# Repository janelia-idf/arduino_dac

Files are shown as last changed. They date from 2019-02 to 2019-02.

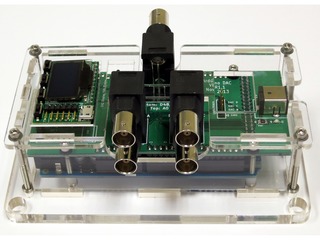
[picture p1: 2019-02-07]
images/arduino_dac_04_s.jpg

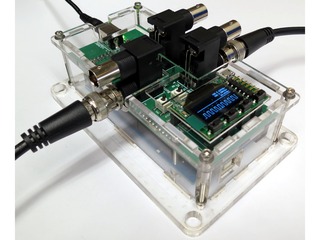
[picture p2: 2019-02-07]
images/arduino_dac_08_s.jpg

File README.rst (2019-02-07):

===========
Arduino DAC
===========

Arduino-based digital to analog converter.

firmware
========

Contains the Arduino firmware files. See firmware/README.rst

host
====

Contains the code for controlling with a host computer.

python
------

See host/python/README.rst

pcb
===

Contains the arduino_dac pcb Kicad and gerber files.

Author: Peter Polidoro

This program is free software: you can redistribute it and/or modify
it under the terms of the GNU Lesser General Public License as published by
the Free Software Foundation, either version 3 of the License, or
(at your option) any later version.

This program is distributed in the hope that it will be useful,
but WITHOUT ANY WARRANTY; without even the implied warranty of
MERCHANTABILITY or FITNESS FOR A PARTICULAR PURPOSE.  See the
GNU Lesser General Public License for more details.

You should have received a copy of the GNU Lesser General Public License
along with this program.  If not, see <http://www.gnu.org/licenses/>.

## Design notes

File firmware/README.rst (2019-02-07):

Arduino DAC Device Firmware
---------------------------

Arduino firmware for the arduino_dac device.

For see the INSTALL.rst for installation instructions.

arduino_relay_controller device firmware may be freely distributed and
modified in accordance with the License.

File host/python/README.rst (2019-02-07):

===========
arduino_dac
===========

arduino_dac is a python package to control the Arduino DAC over USB,
using the python module, the command line, or a webpage using a
webserver.

Install
-------

See INSTALL.rst

Running
=======

* If installed into a virtual environment, activate the virtual
  environment before running::

    source ~/virtualenvs/arduino_dac/bin/activate

Python Module
-------------

Typical usage often looks like this::

    from arduino_dac import ArduinoDac

Web Page Controls
-----------------

Open a terminal and run::

    arduino_dac_webserver.py

Open a browser and navigate to::

    http://localhost:5000

Author: Peter Polidoro

This program is free software: you can redistribute it and/or modify
it under the terms of the GNU Lesser General Public License as published by
the Free Software Foundation, either version 3 of the License, or
(at your option) any later version.

This program is distributed in the hope that it will be useful,
but WITHOUT ANY WARRANTY; without even the implied warranty of
MERCHANTABILITY or FITNESS FOR A PARTICULAR PURPOSE.  See the
GNU Lesser General Public License for more details.

You should have received a copy of the GNU Lesser General Public License
along with this program.  If not, see <http://www.gnu.org/licenses/>.

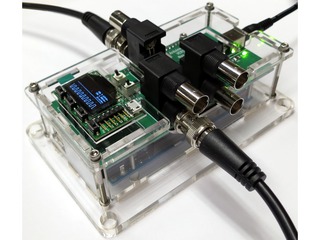
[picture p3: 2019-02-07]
images/arduino_dac_07_s.jpg

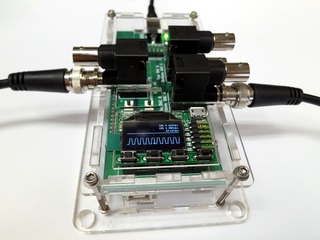
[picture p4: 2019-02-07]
images/arduino_dac_06_s.jpg

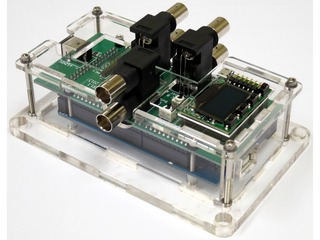
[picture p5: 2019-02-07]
images/arduino_dac_02_s.jpg

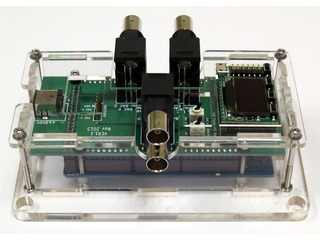
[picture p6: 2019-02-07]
images/arduino_dac_05_s.jpg

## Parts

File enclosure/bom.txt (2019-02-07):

-*- mode:org -*-

# Bill of Materials
| ! | description                                                                                                    | vendor   | part number | quantity |  cost |
|---+----------------------------------------------------------------------------------------------------------------+----------+-------------+----------+-------|
|   | 18-8 Stainless Steel Socket Head Cap Screw, 4-40 Thread, 1-1/2" Length                                         | mcmaster | 92196A119   |        4 |  0.09 |
|   | 18-8 Stainless Steel Socket Head Cap Screw, 4-40 Thread, 1" Length                                             | mcmaster | 92196A115   |        4 |  0.06 |
|   | 300 Series Stainless Steel Mil Spec Flat Washer, Number 4 Size, .25" OD, .02"-.03" Thickness, NASM/MS15795-803 | mcmaster | 98019A309   |        4 |  0.01 |
|   | Nylon 6/6 General Purpose Flat Washer, Number 4 Screw Size, .21" OD, .04"-.06" Thick                           | mcmaster | 90295A340   |        4 |  0.05 |
|   | Nylon Unthreaded Spacer, 3/16" OD, 3/16" Length, #4 Screw Size                                                 | mcmaster | 94639A615   |        4 |  0.07 |
|   | 18-8 Stainless Steel Broach Style Captive Nut, 4-40 Thread Size, .060" Minimum Panel Thickness                 | mcmaster | 94648A320   |        8 |  0.40 |
|   | Optically Clear Cast Acrylic Sheet, 1/8" Thick, 12" x 12"                                                      | mcmaster | 8560K239    |        1 |  8.63 |
|   | Optically Clear Cast Acrylic Sheet, 1/4" Thick, 12" x 12"                                                      | mcmaster | 8560K354    |        1 | 16.36 |
|---+----------------------------------------------------------------------------------------------------------------+----------+-------------+----------+-------|
| # | total                                                                                                          |          |             |          | 29.31 |
#+TBLFM: @10$6=(@I$quantity..@II$quantity)*(@I$cost..@II$cost);%.2f;N

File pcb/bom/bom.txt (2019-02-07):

-*- mode:org -*-

# Opt101.lst
| ref     | value                    |
|---------+--------------------------|
| C1      | 1.5uF                    |
| C2      | 1.5uF                    |
| C3      | 1.5uF                    |
| C4      | 1.5uF                    |
| C5      | 10uF                     |
| C6      | 0.1uF                    |
| C7      | 0.1uF                    |
| C8      | 10uF                     |
| C9      | 0.1uF                    |
| D1      | AD57X4R                  |
| D2      | LED                      |
| P1      | +12VDC                   |
| P2      | DBNC_INPUT               |
| P3      | DBNC_OUTPUT_AB           |
| P4      | DBNC_OUTPUT_CD           |
| P5      | CONN_5                   |
| R1      | 0.1                      |
| R2      | 0.1                      |
| R3      | 0.1                      |
| R4      | 0.1                      |
| R5      | 330                      |
| SHIELD1 | ARDUINO_MEGA_SHIELD_FULL |
| SW1     | SWITCH_INPUT             |
| SW2     | SWITCH_OUTPUT            |
| X1      | XPROTOLAB                |

# Bill of Materials
| ! | part    | description                      | vendor      | part number     | quantity |   cost |
|---+---------+----------------------------------+-------------+-----------------+----------+--------|
|   | PCB     | arduino_dac                      | pcbuniverse | v1.1            |        1 |   1.00 |
|   | C1-4    | CAP CER 1.5UF 25V 10% X7R 1210   | digikey     | 445-13384-1-ND  |        4 |   0.84 |
|   | C5,8    | CAP TANT 10UF 25V 10% 1210       | digikey     | 478-5257-1-ND   |        2 |   1.06 |
|   | C6,7,9  | CAP CER 0.1UF 50V 10% X7R 1210   | digikey     | 478-3586-1-ND   |        3 |   0.34 |
|   | D1      | IC DAC 16BIT DSP/SRL 24TSSOP     | digikey     | AD5754RBREZ-ND  |        1 |  24.75 |
|   | D2      | LED GREEN CLEAR 0805 SMD         | digikey     | 160-1179-1-ND   |        1 |   0.35 |
|   | P1      | CONN PWR JACK DC 2.1X5.5 8A T/H  | digikey     | CP-063AH-ND     |        1 |   1.78 |
|   | P1      | TRANSFORMER DESK TOP 12V 18W     | digikey     | T1196-P5P-ND    |        1 |  16.37 |
|   | P2-4    | CONN BNC JACK R/A 75 OHM PCB     | digikey     | ACX1655-ND      |        3 |  11.10 |
|   | P5      | CONN HEADER 5POS .100" SGL GOLD  | digikey     | SAM1031-05-ND   |        1 |   0.89 |
|   | R1-4    | RES 0.1 OHM 1/3W 1% 1210 SMD     | digikey     | P100NACT-ND     |        4 |   0.78 |
|   | R5      | RES 330 OHM 1/4W 5% 1210 SMD     | digikey     | RHM330BECT-ND   |        1 |   0.18 |
|   | SHIELD1 | BOARD MCU MEGA2560               | digikey     | 1050-1018-ND    |        1 |  51.91 |
|   | SHIELD1 | CONN HDR VERT 50POS .100" SNGL   | digikey     | SAM1055-50-ND   |        4 |   3.42 |
|   | SW1-2   | SWITCH TOGGLE SPDT 0.4VA 20V     | digikey     | CKN1784CT-ND    |        2 |   5.63 |
|   | X1      | XMEGA Xprotolab                  | gabotronics | XMEGA Xprotolab |        1 |  49.00 |
|   | X1      | CONN HEADER FMALE 12POS .1" GOLD | digikey     | S7045-ND        |        1 |   0.99 |
|   | X1      | CONN HEADER FEMALE 2POS .1" GOLD | digikey     | S7035-ND        |        4 |   0.49 |
|---+---------+----------------------------------+-------------+-----------------+----------+--------|
| # | total   |                                  |             |                 |          | 217.04 |
#+TBLFM: @20$7=(@I$quantity..@II$quantity)*(@I$cost..@II$cost);%.2f;N

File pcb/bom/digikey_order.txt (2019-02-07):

445-13384-1-ND, 50
478-5257-1-ND, 50
478-3586-1-ND, 50
160-1179-1-ND, 50
SAM1031-05-ND, 50
P100NACT-ND, 50
RHM330BECT-ND, 50
SAM1055-50-ND, 50
RHM0.0BECT-ND, 100
CKN1784CT-ND, 20

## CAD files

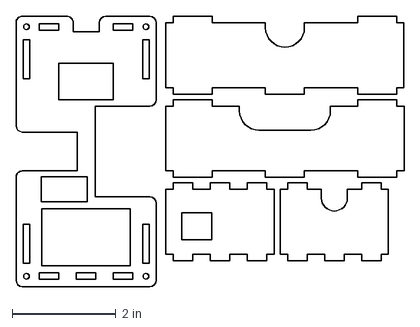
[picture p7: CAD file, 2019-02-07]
enclosure/arduino_enclosure_dac.125in.dxf
7.46 x 5.20 in

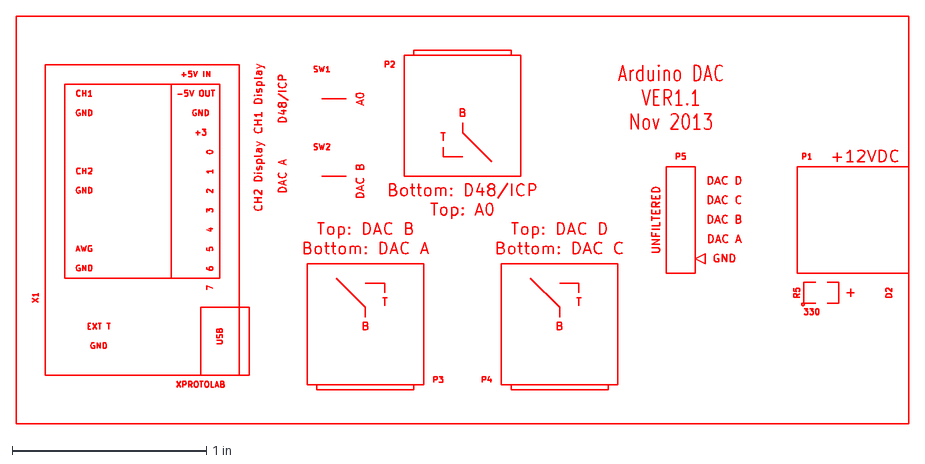
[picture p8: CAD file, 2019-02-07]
pcb/v1.1/dxf/arduino_dac-SilkS_Front.dxf
4.60 x 2.10 in

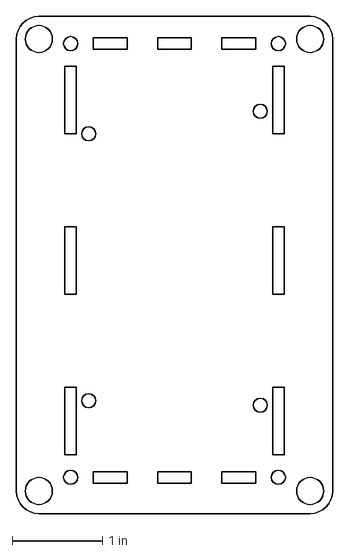
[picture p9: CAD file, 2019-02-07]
enclosure/arduino_enclosure_dac.25in.dxf
3.50 x 5.50 in

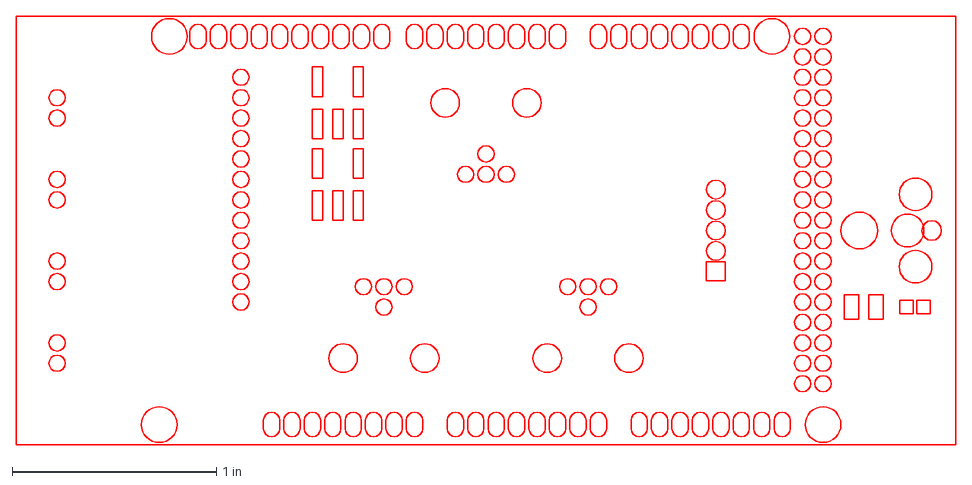
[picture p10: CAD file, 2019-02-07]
pcb/v1.1/dxf/arduino_dac-Mask_Front.dxf
4.60 x 2.10 in

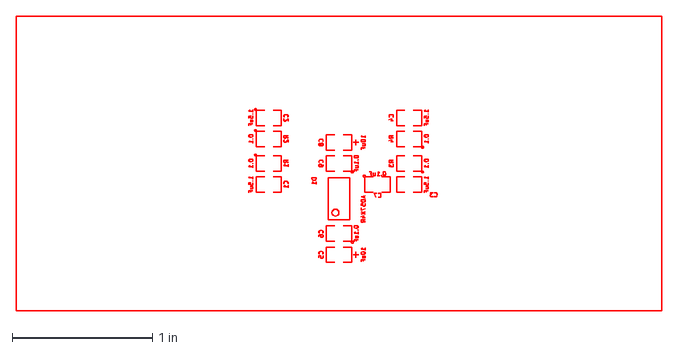
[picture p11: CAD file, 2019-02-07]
pcb/v1.1/dxf/arduino_dac-SilkS_Back.dxf
4.60 x 2.10 in

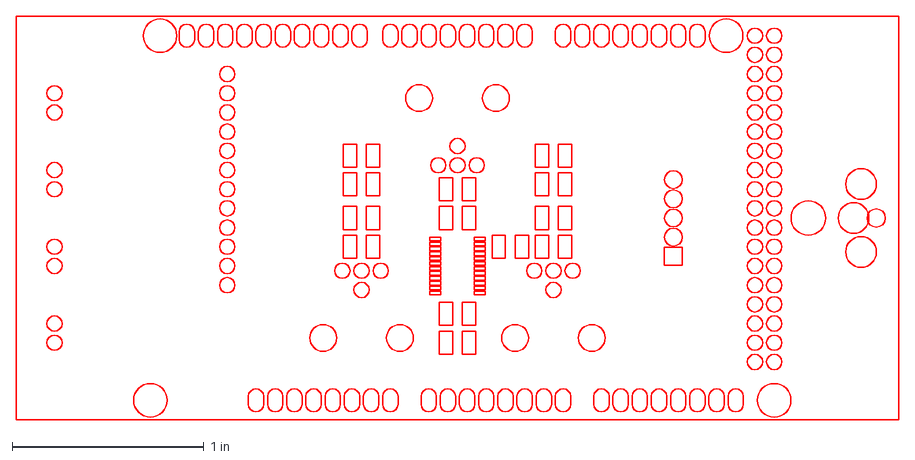
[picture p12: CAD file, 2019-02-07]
pcb/v1.1/dxf/arduino_dac-Mask_Back.dxf
4.60 x 2.10 in

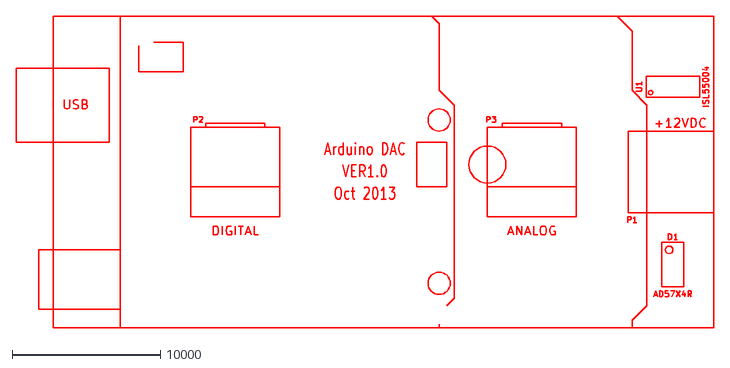
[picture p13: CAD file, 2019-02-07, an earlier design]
pcb/v1.0/dxf/arduino_dac-SilkS_Front.dxf
47000.0 x 21000.0

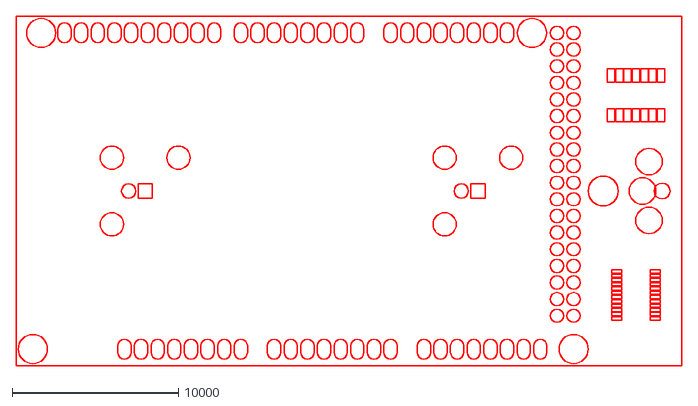
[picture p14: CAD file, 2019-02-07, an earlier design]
pcb/v1.0/dxf/arduino_dac-Mask_Front.dxf
40000.0 x 21000.0

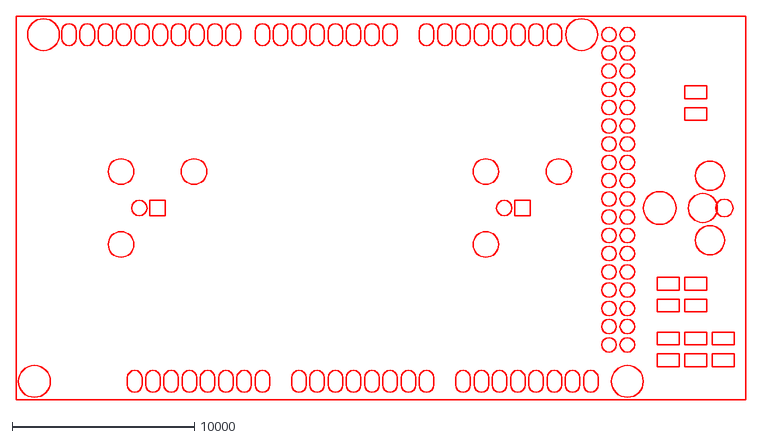
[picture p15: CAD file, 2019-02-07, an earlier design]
pcb/v1.0/dxf/arduino_dac-Mask_Back.dxf
40000.0 x 21000.0

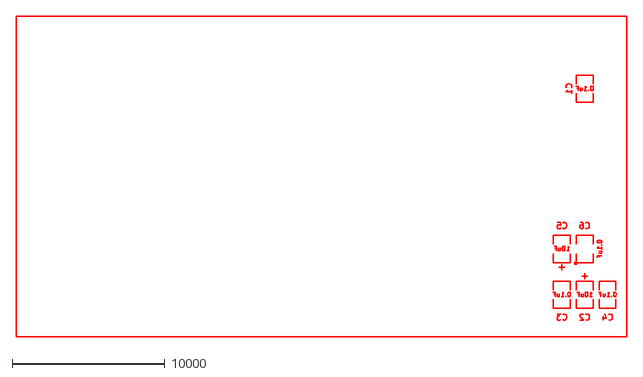
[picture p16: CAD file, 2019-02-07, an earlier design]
pcb/v1.0/dxf/arduino_dac-SilkS_Back.dxf
40000.0 x 21000.0

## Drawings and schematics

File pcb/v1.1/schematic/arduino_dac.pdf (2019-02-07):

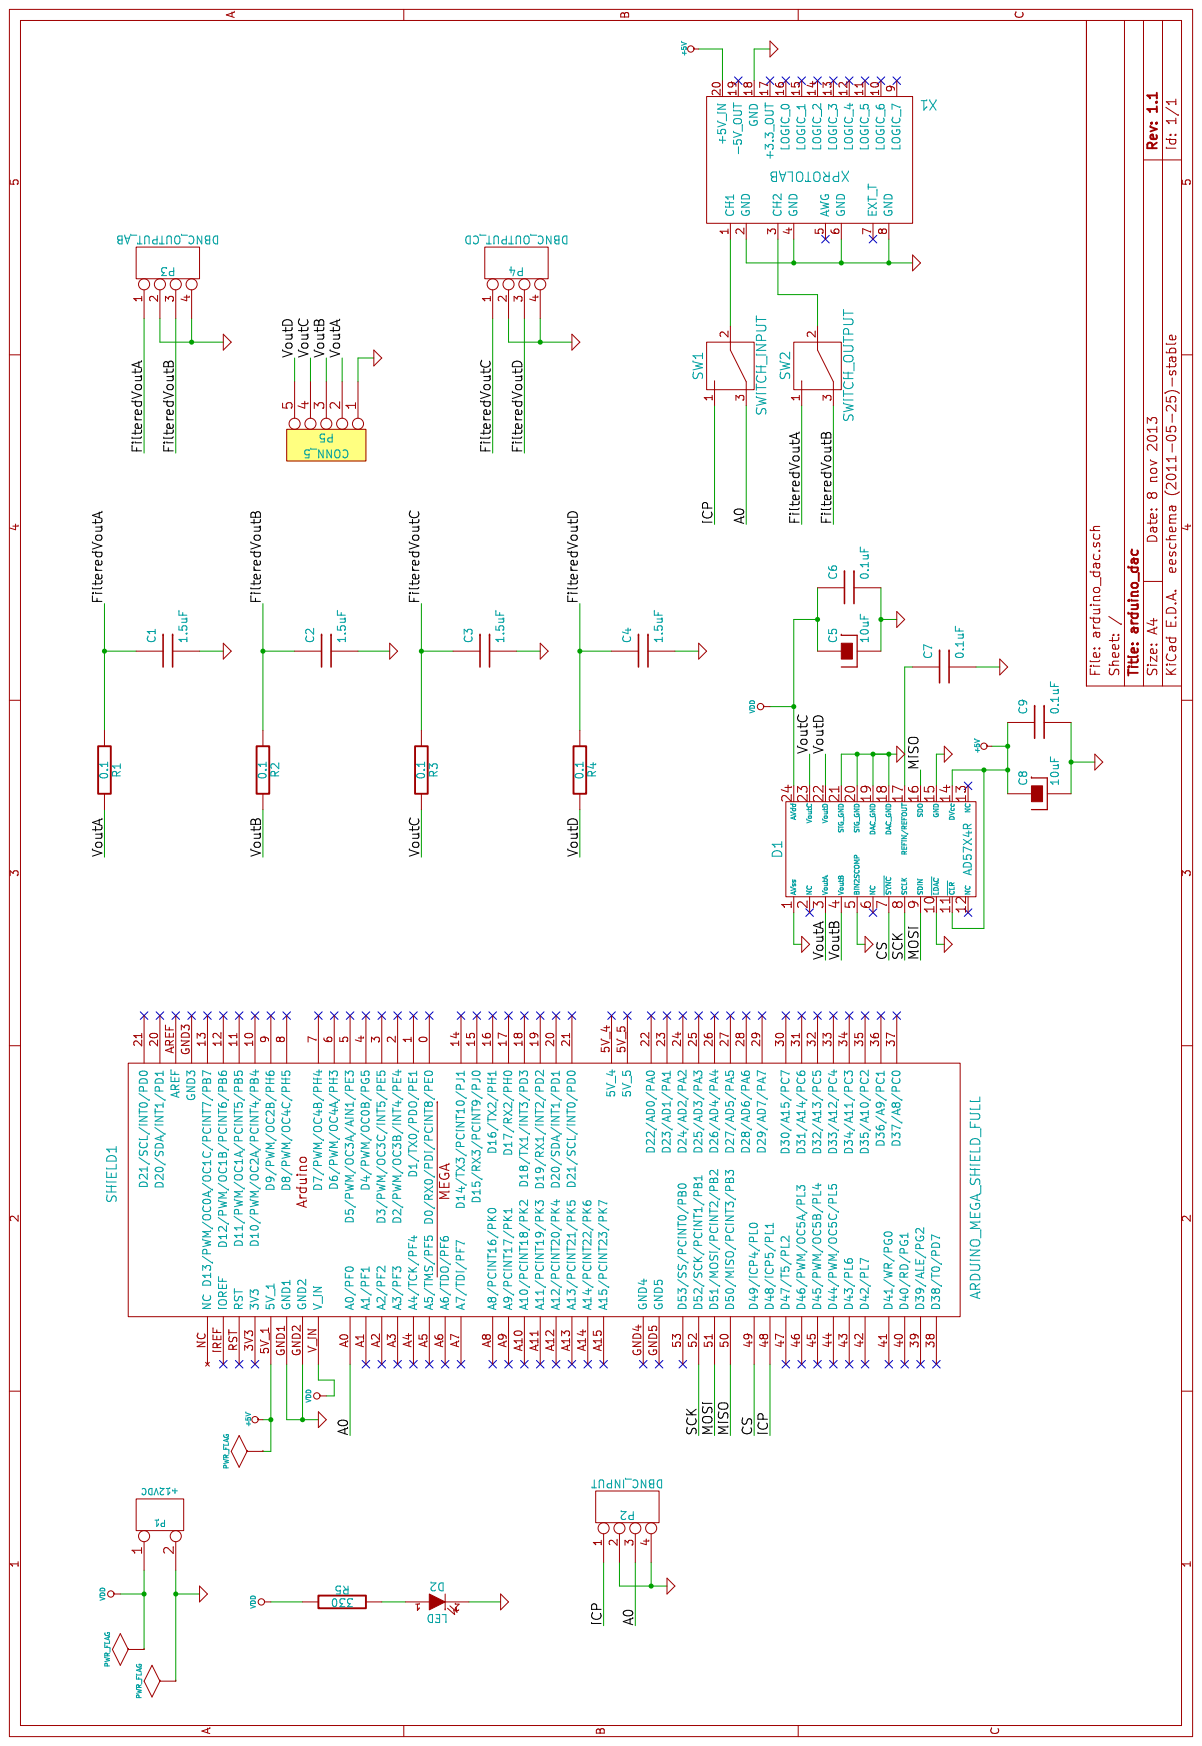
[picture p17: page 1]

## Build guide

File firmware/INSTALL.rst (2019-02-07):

Firmware installation instructions
-----------------------------------

Requirements:

The following libraries should be placed in the arduino sketchbook libraries
directory.

* Streaming         https://bitbucket.org/peterpolidoro/arduino_libs/src
* SerialReceiver    https://bitbucket.org/peterpolidoro/arduino_libs/src
* DictPrinter       https://bitbucket.org/peterpolidoro/arduino_libs/src
* AD57x4r           https://bitbucket.org/peterpolidoro/arduino_libs/src

Build and upload the firmware using the Arduino IDE.

see http://arduino.cc/en/Guide/Environment for instructions on using the IDE.

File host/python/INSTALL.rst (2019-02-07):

arduino_dac installation instructions
-------------------------------------

* Create a new virtual environment if necessary::

    virtualenv --system-site-packages ~/virtualenvs/arduino_dac

* Activate a virtual environment::

    source ~/virtualenvs/arduino_dac/bin/activate

* Install dependencies::

    pip install flask --upgrade
    pip install flask-sijax --upgrade

* Clone bitbucket mercurial repositories::

    mkdir ~/mercurial
    cd ~/mercurial
    hg clone https://bitbucket.org/peterpolidoro/python_libs/
    hg clone https://bitbucket.org/peterpolidoro/arduino_dac/

* Install python packages::

    cd ~/mercurial/python_libs/arduino_device
    python cleanup.py
    python setup.py install
    cd ~/mercurial/arduino_dac/host/python
    python cleanup.py
    python setup.py install

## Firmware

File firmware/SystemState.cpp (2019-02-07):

#if defined(ARDUINO) && ARDUINO >= 100
#include "Arduino.h"
#else
#include "WProgram.h"
#endif
#include "string.h"
#include "SystemState.h"

SystemState::SystemState() {
  setErrMsg("");
}

void SystemState::setErrMsg(char *msg) {
  strncpy(errMsg,msg,SYS_ERR_BUF_SZ);
}

void SystemState::initialize() {
  dac = AD57X4R(constants::dacCsPin);

  // Initialize SPI:
  SPI.setDataMode(SPI_MODE2);
  SPI.setBitOrder(MSBFIRST);
  SPI.setClockDivider(SPI_CLOCK_DIV2);
  SPI.begin();

  // Initialize DAC
  dac.init(AD57X4R::AD5754R, AD57X4R::UNIPOLAR_5V, AD57X4R::ALL);
  dac_max_value = dac.getMaxDacValue();

  // Initialize time triggered scheduler
  tts.init();
  updateTaskId = -1;
}

bool SystemState::analogWriteChannel(AD57X4R::channels channel, int milli_volt) {
  unsigned int value = map(milli_volt,constants::milliVoltMin,constants::milliVoltMax,0,dac_max_value);
  dac.analogWrite(channel,value);
  return true;
}

bool SystemState::analogWriteA(int milli_volt) {
  analogWriteChannel(AD57X4R::A,milli_volt);
  return true;
}

bool SystemState::analogWriteB(int milli_volt) {
  analogWriteChannel(AD57X4R::B,milli_volt);
  return true;
}

bool SystemState::analogWriteC(int milli_volt) {
  analogWriteChannel(AD57X4R::C,milli_volt);
  return true;
}

bool SystemState::analogWriteD(int milli_volt) {
  analogWriteChannel(AD57X4R::D,milli_volt);
  return true;
}

bool SystemState::analogWriteAll(int milli_volt) {
  analogWriteChannel(AD57X4R::ALL,milli_volt);
  return true;
}

bool SystemState::startWaveform(int waveform) {
  stopWaveform();
  int update_rate = 5;
  int count = -1;
  tts.setTime(0);
  updateTaskId = (int)tts.addTaskUsingDelay(100,inlineUpdate,waveform,update_rate,count,false);
  return true;
}

bool SystemState::stopWaveform() {
  if (updateTaskId >= 0) {
    tts.removeTask((uint8_t)updateTaskId);
    updateTaskId = -1;
  }
  return true;
}

bool SystemState::update(int waveform) {
  int period = 1000;
  int amplitude = 5000;
  int milli_volt = 0;
  int cycle_time = tts.ms()%period;
  if (waveform == 0) {
    float angle = (6.2832*cycle_time)/period;
    double value = sin(angle);
    milli_volt = value*amplitude/2 + amplitude/2;
  } else if (waveform == 1) {
    if (cycle_time <= period/2) {
      milli_volt = 2*(amplitude/period)*cycle_time;
    } else {
      milli_volt = amplitude - 2*(amplitude/period)*(cycle_time - period/2);
    }
  } else if (waveform == 2) {
    milli_volt = (amplitude/period)*cycle_time;
  } else if (waveform == 3) {
    if (cycle_time <= period/2) {
      milli_volt = amplitude;
    } else {
      milli_volt = 0;
    }
  }
  analogWriteA(milli_volt);
  return true;
}

SystemState systemState;

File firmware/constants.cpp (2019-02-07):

#include "constants.h"
namespace constants {
  // Communications parameters
  const int baudrate = 9600;

  // Device parameters
  const int modelNumber = 2486;
  const int serialNumberMin = 0;
  const int serialNumberMax = 255;
  const int firmwareNumber = 0;

  // Pin assignment
  const int dacCsPin = 49;

  // Dac parameters
  const int milliVoltMin = 0;
  const int milliVoltMax = 5000;

  // Waveform parameters
  const int waveformMin = 0;
  const int waveformMax = 3;

}

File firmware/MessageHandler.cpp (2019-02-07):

#include <util/atomic.h>
#include "MessageHandler.h"
#include "Streaming.h"
#include "SystemState.h"

enum {
  cmdGetDevInfo,                    // Done
  cmdGetCmds,                       // Done
  cmdGetRspCodes,                   // Done
  cmdSetSerialNumber,               //

  cmdAnalogWriteA,                 //
  cmdAnalogWriteB,                 //
  cmdAnalogWriteC,                 //
  cmdAnalogWriteD,                 //
  cmdAnalogWriteAll,                 //

  cmdStartWaveform,                 //
  cmdStopWaveform,                 //

  // DEVELOPMENT
  cmdDebug,
};


const int rspSuccess = 1;
const int rspError = 0;

void MessageHandler::processMsg() {
  while (Serial.available() > 0) {
    process(Serial.read());
    if (messageReady()) {
      msgSwitchYard();
      reset();
    }
  }
  return;
}

void MessageHandler::msgSwitchYard() {
  int cmd = readInt(0);
  dprint.start();
  dprint.addIntItem("cmd_id", cmd);

  switch (cmd) {

  case cmdGetDevInfo:
    handleGetDevInfo();
    break;

  case cmdGetCmds:
    handleGetCmds();
    break;

  case cmdGetRspCodes:
    handleGetRspCodes();
    break;

  case cmdSetSerialNumber:
    handleSetSerialNumber();
    break;

  case cmdAnalogWriteA:
    handleAnalogWriteA();
    break;

  case cmdAnalogWriteB:
    handleAnalogWriteB();
    break;

  case cmdAnalogWriteC:
    handleAnalogWriteC();
    break;

  case cmdAnalogWriteD:
    handleAnalogWriteD();
    break;

  case cmdAnalogWriteAll:
    handleAnalogWriteAll();
    break;

  case cmdStartWaveform:
    handleStartWaveform();
    break;

  case cmdStopWaveform:
    handleStopWaveform();
    break;

  // DEVELOPMENT
  case cmdDebug:
    handleDebug();
    break;

  default:
    dprint.addIntItem("status", rspError);
    dprint.addStrItem("err_msg", "unknown command");
    break;
  }
  dprint.stop();
}

void MessageHandler::handleGetCmds() {
  dprint.addIntItem("status", rspSuccess);
  dprint.addIntItem("getDevInfo", cmdGetDevInfo);
  dprint.addIntItem("getCmds", cmdGetCmds);
  dprint.addIntItem("getRspCodes", cmdGetRspCodes);
  dprint.addIntItem("setArduinoSerialNumber", cmdSetSerialNumber);

  dprint.addIntItem("analogWriteA", cmdAnalogWriteA);
  dprint.addIntItem("analogWriteB", cmdAnalogWriteB);
  dprint.addIntItem("analogWriteC", cmdAnalogWriteC);
  dprint.addIntItem("analogWriteD", cmdAnalogWriteD);
  dprint.addIntItem("analogWriteAll", cmdAnalogWriteAll);

  dprint.addIntItem("startWaveform", cmdStartWaveform);
  dprint.addIntItem("stopWaveform", cmdStopWaveform);

  // DEVELOPMENT
  dprint.addIntItem("cmdDebug", cmdDebug);
}

void MessageHandler::handleGetDevInfo() {
  dprint.addIntItem("status", rspSuccess);
  dprint.addIntItem("model_number",  constants::modelNumber);
  dprint.addIntItem("serial_number", savedVariables.getSerialNumber());
  dprint.addIntItem("firmware_number", constants::firmwareNumber);
}

bool MessageHandler::checkNumberOfArgs(int num) {
  bool flag = true;
  if (numberOfItems() != num) {
    dprint.addIntItem("status", rspError);
    dprint.addStrItem("err_msg", "incorrect number of arguments");
    flag = false;
  }
  return flag;
}

bool MessageHandler::checkSerialNumberArg(int serial_number) {
  bool flag = true;
  if ((serial_number<constants::serialNumberMin) || (constants::serialNumberMax<serial_number)) {
    dprint.addIntItem("status", rspError);
    dprint.addStrItem("err_msg", "serial number argument out of range");
    flag = false;
  }
  return flag;
}

void MessageHandler::systemCmdRsp(bool flag) {
  if (flag) {
    dprint.addIntItem("status", rspSuccess);
  }
  else {
    dprint.addIntItem("status", rspError);
    dprint.addStrItem("err_msg", systemState.errMsg);
  }
}

void MessageHandler::handleGetRspCodes() {
  dprint.addIntItem("status", rspSuccess);
  dprint.addIntItem("rsp_success",rspSuccess);
  dprint.addIntItem("rsp_error", rspError);
}

void MessageHandler::handleSetSerialNumber() {
  if (!checkNumberOfArgs(2)) {return;}
  int serialNumber = readInt(1);
  if (checkSerialNumberArg(serialNumber)) {
    systemCmdRsp(savedVariables.setSerialNumber(serialNumber));
  }
}

bool MessageHandler::checkMilliVoltArg(int milli_volt) {
  bool flag = true;
  if ((milli_volt<constants::milliVoltMin) || (constants::milliVoltMax<milli_volt)) {
    dprint.addIntItem("status", rspError);
    dprint.addStrItem("err_msg", "milli_volt argument out of range");
    flag = false;
  }
  return flag;
}

bool MessageHandler::checkWaveformArg(int waveform) {
  bool flag = true;
  if ((waveform<constants::waveformMin) || (constants::waveformMax<waveform)) {
    dprint.addIntItem("status", rspError);
    dprint.addStrItem("err_msg", "waveform argument out of range");
    flag = false;
  }
  return flag;
}

void MessageHandler::handleAnalogWriteA() {
  if (!checkNumberOfArgs(2)) {return;}
  int milli_volt = readInt(1);
  if (checkMilliVoltArg(milli_volt)) {
    systemState.stopWaveform();
    systemCmdRsp(systemState.analogWriteA(milli_volt));
  }
}

void MessageHandler::handleAnalogWriteB() {
  if (!checkNumberOfArgs(2)) {return;}
  int milli_volt = readInt(1);
  if (checkMilliVoltArg(milli_volt)) {
    systemState.stopWaveform();
    systemCmdRsp(systemState.analogWriteB(milli_volt));
  }
}

void MessageHandler::handleAnalogWriteC() {
  if (!checkNumberOfArgs(2)) {return;}
  int milli_volt = readInt(1);
  if (checkMilliVoltArg(milli_volt)) {
    systemState.stopWaveform();
    systemCmdRsp(systemState.analogWriteC(milli_volt));
  }
}

void MessageHandler::handleAnalogWriteD() {
  if (!checkNumberOfArgs(2)) {return;}
  int milli_volt = readInt(1);
  if (checkMilliVoltArg(milli_volt)) {
    systemState.stopWaveform();
    systemCmdRsp(systemState.analogWriteD(milli_volt));
  }
}

void MessageHandler::handleAnalogWriteAll() {
  if (!checkNumberOfArgs(2)) {return;}
  int milli_volt = readInt(1);
  if (checkMilliVoltArg(milli_volt)) {
    systemState.stopWaveform();
    systemCmdRsp(systemState.analogWriteAll(milli_volt));
  }
}

void MessageHandler::handleStartWaveform() {
  if (!checkNumberOfArgs(2)) {return;}
  int waveform = readInt(1);
  if (checkWaveformArg(waveform)) {
    systemCmdRsp(systemState.startWaveform(waveform));
  }
}

void MessageHandler::handleStopWaveform() {
  systemCmdRsp(systemState.stopWaveform());
}

// -------------------------------------------------


void MessageHandler::handleDebug() {
  char name[20];
  dprint.addIntItem("status", rspSuccess);
}


MessageHandler messageHandler;
